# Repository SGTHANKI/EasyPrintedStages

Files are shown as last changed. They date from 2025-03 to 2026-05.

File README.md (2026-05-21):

# EasyPrintedStages
A set of 3D printed open sourced motion stages for scientific and laboratory work compatible with the gridfinity standard. The latest "stable" (version printed and tested) release can be found on the printables linked below. Please consider going there and like/download as it helps me out!
There are two different compatible stages in this ecosystem, a linear and rotary stage. A Z stage, pitch stage, and motorised stages are currently under development. You may see those in this repo but they are "alpha" versions uploaded to the master branch for collaborators to test before we fully release them. 

This readme is long but includes all the instructions you need to build and assemble the stages. __IF PRINTING A LINEAR STAGE CHECK THE LEADSCREW PRINTING GUIDE FIRST FOR BEST RESULTS__.
# Content:
- Build Options for All Stages
- Linear Stage Specific Build Options
- Linear Stage Printing Instructions
- Linear Stage Assembly Instructions
- Rotary Stage Prtinting Instructions
- Rotary Stage Assembly Instructions
- Motorised Stage Instructions

# Build Options for All Stages:
The design is built to be as modular as possible and users are encouraged to download FreeCAD and export the model to 3mf files for printer directly from the CAD files instead of using those provided. Numerous mounting solutions are also provided for the stage. 
## Optional Gridfinity Standard Mounting Plate:
The FreeCAD design makes use of the Gridfinity Workbench within FreeCAD. Users can find instructions on how to install and use this workbench under its associated page Gridfinity Workbench. A 2x2 unit Gridfinity base plate is provided in the design that can be screwed into the base of the stage. Additionally a 4x4 unit bolt together mesh is provided to act as a starting point for mounting a Gridfinity based stage system. 
Pasted image 20250202160743
Mounting bolts for the Gridfinity base plate go through the magnet holes on the plate base. __Note: If you make a custom base larger than 2x2u, you will need to quickly pocket the holes all the way through the plate. This has already been done on the provided 2x2u base.__
Easy Stage In Mesh Cover 1
## Optional Top Plate
Pasted image 20250202161026
An optional top plate can be printed with the design. It mounts via 4 M3 bolts in the corners of the plate. The other 2 holes in the plate are for locking bolts, these holes go all the way through the top plate of the stage and allow a longer 25mm M3 bolt to be tightened down into the base of the stage, locking it in place. This can be used to lock the stage in a desired position. 

The mounting plate features a grid of 2.6mm diameter holes, these are the perfect size for M3 bolts to thread into without the need for threaded inserts. The holes are spaced 5mm apart to make designing custom mounting hardware as easy as possible. Some hardware for this plate has been provided, namely the Easy Stage Clamp. 
### How to make a custom mounting plate:
Open the design in FreeCAD and activate the Mounting Plate Body. The final operation is the one that pockets all the mounting holes, simply deleting this operation or copying the body from the previous operation will yield a blank plate that can be modified however is 
Pasted image 20250202161508
Pasted image 20250202161528
## How to Mount Other Stages From The Ecosystem:
All of the Easy Printed Stages can be mounted to each other via the holes on their top.
Cover Linear Best
__NOTE ON ROTARY STAGE__ Only two mounting bolts are accessible, these should be more than enough to hold it down but because of how the case halves are tightened down together a second pair of holes would never line up. 
# Linear Stage Specific Build Options:
##Rubber Band For Anti-Backlash
You can loop a rubber band between the threaded nut and the two holes where the adjustor protrudes from the base to apply a constant force onto the lead screw. This is generally not needed if printed at higher tolerance but was included for users using older printers without input shaping. 

# Linear Stage Printing Instructions:
The design should be printed in 2 separate sets. These are documented here. __PLEASE CHECK THE LEAD SCREW SETTINGS BELOW OR IT WILL FAIL TO PRINT!__
## Bulk, Low Tolerance Components
Parts in this set are: 
- Base Plate with Integrated Gridfinity
- Shim
- Upper
- Adjuster Cap
- Base
- M3 5mm Spaced Mounting Plate
- 2u Gridfinity Base Plate

__Recommended Materials for This Set:__
- PETG --> Best overall and chemically resistant so good for use in the lab. 
- PETG CF --> Much stronger than regular PETG but surface is rougher and parts can be less clean/may need sanding. Also more expensive.
- PLA --> Cheapest and easiest to print but not chemically resistant so use only in non-wet lab's. 

You can also use pretty much anything else you want provided its mechanically hard but increasing the strength of these parts does little for the designs overall strength since the weakest point is the printed lead screw. 

__Print Settings and Other Info:__
- You can get away with a 0.6 or 0.8mm nozzle on this set to improve print time but the fit/finish will be worse. __0.4mm is recommended__. There is no need to use high detail slicer parameters. 
- __Enable support__ for the Base and Base Plate with Integrated Gridfinity parts, the overhand here needs it. Tree supports are recommended and if a __threshold angle of 30 degrees__ is used in the slicer only this region of the design will be supported by Tree's. //this was tested in Bambu, Orca, and Prusa slicer. 

3mf project files for this set have been made for Bambu Studio (specifically for the A1 Mini but can easily be adapted to their other printers) and Prusa slicer, they can be found within the GitHub for the project. 
## High Tolerance Threaded Parts
Parts in this set are: 
- Adjuster
- Thread Block Modelled

__Recommended Materials for This Set:__
- PETG --> Best if you only have a low temperature printer.
- ASA --> Best if you have a high temperature printer but chemical resistance isn't a concern. 
- PET --> Best for high temperature and chemical resistance but hard to print well. 

*Note on PLA: You can use it but it may not be strong enough nor is it chemically resistant.* 

*Note on CF/GF reinforced filaments: They can be used here but there is a concern about their abrasive nature wearing down the threads over time.* 

__Print Settings and Other Info:__
- Use a 0.4 or 0.2mm nozzle.
- Use 100% infill.
- Use the highest detail setting on the slicer of your choice, less because of detail, more because it will slow the printer down making the long tall lead screw print easier. 
- If you cannot use the provided 3mf for the Adjuster __HAVE A LOOK AT IT FIRST BELOW__. Custom painted on supports are used to stabilise the tall and wobbly part and make it print well. Open that model and see how I've done it before trying to print it yourself. I used the paint on custom support tool in the slicer with the tree supports. Make sure not to paint them onto the threads or it will ruin the threads, paint them on just after the threads finish at the top of the adjuster. 
Supported Leadscrew
Support Enforcers on Outside of Leadscrew
Support Enforcer in Top of Leadscrew

# Linear Stage Assembly Instructions:
## Important Note: 
Use silicone grease on the way and lead screw to make the stage move easier and last longer. 
## Step 1: Thread the Adjuster
Apply a small amount of Silicone Grease to the adjuster tip and to the holes made for it in the base of the stage, thread the adjuster through the block and then apply the end cap with an M3x5mm bolt. At this stage you should also apply Silicone Grease to the ways of the stage. You're assembly should look like the one seen below:
Step 1 Photo
__Note: The direction of the little triangle on the top of the thread block doesn't matter, its for a different project that re-uses these parts.__
## Step 2: Mount Upper
Insert the longer M3 bolts into the side of the upper but leave some space, you only want about 2mm of the bolt to protrude into the way, as seen below: 
step 2 alt angle photo
Slide the upper over the lower assembly from __STEP 1__, you dont need to put the shim in yet. You'll feel the top seat itself down onto the threaded block with a click, once you feel this you can tighten the two M3 bolts on the top.
step 2 no way
__Note: There is a vernier gauge modelled on the side of the base and the top piece, make sure you have the top piece the right way round if you plan on using these. The top is ambidextrous so if you get this wrong the stage will still work.__ 
You can now slide the shim in, make sure the holes on the side of the shim face the bolts you partially inserted earlier.
step 2 way insert photo
Slide the shim all the way in and then start to tighten the bolts on the side. 

__Important:__ Tighten each bolt a little at a time alternating between them. After each bolt check to see if moving the stage is hard, if its hard to move you've tightened the bolts too much and should back them off about half a turn. These bolts are what constrain the stage, you want no play (wobble) in the top of the stage but still want to be able to move the stage with little/no resistance. 
step 2 way flush
## Step 3: Mount Any Addons
You can now mount the top plate of a Gridfinity base. In the images above the Gridfinity base was already installed. You're finished stage should look something like this:
Easy Stage Linear Cover Photo
__Note: The stage shown in the image has been etched with a fibre LASER to engrave the text and decals seen__ 

# Rotary Stage Printing Instructions
## Cycloid 
Print the cycloid in PETG (or any other hard material thats not fiber reinforced). Use a 0.4mm or 0.2mm nozzle and high quality print settings. __NO SUPPORT IS NEEDED__
## Worm Gear
Generally the automatic organic supports of most modern slicers can print the work gear just fine with no needed additions. Print with a 0.4 or 0.2mm nozzle (ideally 0.2mm to make the action smoother). See the image below for how it was supported during testing. Printing at 100% infill is recommended for durability but not strictly necessary.
Pasted image 20250216155126
## All Other Parts
These can be printed in any material with either a 0.4 or 0.6mm nozzle. For the parts seen in the Easy Rotary Stage Assembly Instructions below, PETG-CF filament was used with a 0.6mm nozzle. 

# Rotary Stage Assembly Instructions:
## Important Note: 
Just as with the Linear Stage: Silicone Grease is your friend, use more than you think and wipe the excess off after! This stage can bind when first assembled due to small printing defects, spin the stage via the platform not the adjuster a few time to wear those defects down and smooth the action of the stage. 

## Step 1: Mount the Cycloid Gear
Mount the cycloid gear as seen below. The triangle embedded onto the base of the triangle and on the base of the stage will aid in alignment.

__DO NOT FULLY TIGHTEN THE BOLTS.__

Leave about 3mm space between the gear and the base plate. You tighten these later once the rest of the stage is installed. 
Gear Only On Top
Side Cinematic View

## Step 2: Slide the Front Under the Gear
You can now tighten the bolts on top so that there is no play between the cycloid gear and the front of the stage.
Cycloid Gear Installed

## Step 3: Insert the Worm Gear Into the Back Piece with the Spacer Shim
Slide the worm gear into the back of the case. See the pictures below. Its had to see the spacer, its the small "puck" looking part with a small indent on one side, this indent faces away from the worm gear and is pressed against by an M3 bolt which compresses the worm gear to prevent play in the mechanism. 
Shaft Installed Dark
__ENSURE THE SPACER PUCK IS BETWEEN THE WORM GEAR AND THE CASE__
The depression in the centre of the puck should face the case not the worm gear. An M3 bolt screws through the side of the case and pushed against this, removing the play in the cycloid gear. 
Adjustor Shim View
Its hard to see in the image below but an M3 bolt screws into that hole to compress the worm gear and remove any play in the mechanism. 
SIde Adjustor BOlt
## Step 4: Bolt the Front and Back of the Case Together
Assembled Mechanism Top View
There are two M3 counter bored holes on the worm gear side of the casing. Into these two M3 bolts can be placed that will mate with the other side of the case. Tighten these until the two halved are together and can move freely with no play. You may need to adjust this over time as the gears wear into each other. Avoid over tightening. This design will always have backlash due to the lower tolerances on the cycloid gears that make it possible. 

__You will need a long Hex Bit to reach the M3 bolts__
Lower Fully Assembled

## Step 5: Mount the Aligner Plate
The plate with two channels on it fits into the grooves on the front and base parts of the case, there are two bolt holes that lock this into the case and then prevent any movement. These are M3 bolts and have counter bored holes. The other holes in this piece are for either the Gridfinity Standard mounting plates, to mount the box to other Easy Printed Stages, or to mount a universal mounting plate. 
Top Bolted On Best

## Step 6: (OPTIONAL) Mount to Other Stages, Gridfinity Base, Mounting Plate etc..
Cover Gridfinity 4

# Motorised Stage Upgrade


## Build Differences
Under the "Motorised Linear Stage" Folder a different lead screw and base can be found for the standard linear stage. Follow the standard linear stage build instructions but replace the normal lead screw and base with the motorized versions. 

## Motors
The Motorised lead screws will directly interface with any standard 28BYJ stepper motor. The fit is designed to be tight and you may need to heat the lead screw to get it on. It is reccomended a small dot of some form of glue is used to prevent it loosening over time and with use.

## Endstops
Also provided are brackets for Cherry MX Mechanical keyswitches, but the design files are all provided in FreeCAD and anyone can design their own mount for a switch of their choice using the provided mounting holes on the base. Cherry MX switches were used as they are common and cheap but a future planned upgrade is to add a mount for the more precise and compact Omron SS-01. 

## Control System
Currently no electronics or control are provided though this is being worked on in a different repo that will be linked here when published. The 28BYJ motor is very sommon however and numerous arduino, micropython and C libraries exist to control it. Mounting solutions for darlington array style drivers and a base to contain them are provided. Pictured below are the venerable ULN2003 drivers that are commonly shipped alongside the motors, these are reccomended. 


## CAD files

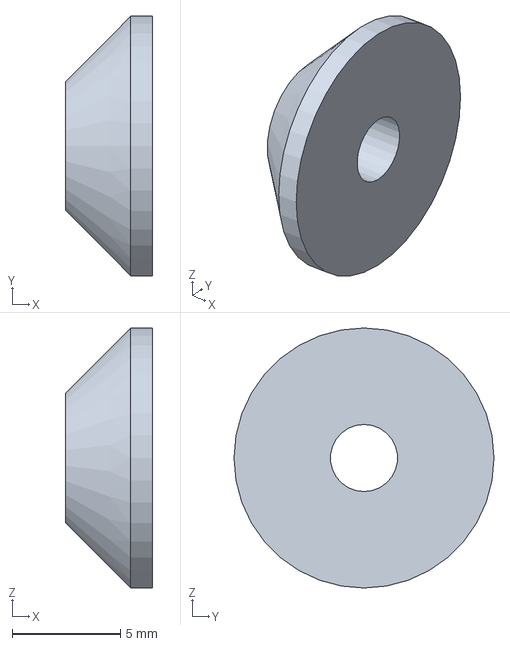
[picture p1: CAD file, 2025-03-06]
Clamp For Aluminium Extrusion/3mf Files/20mmAluClampPV1-Spring Retainer.3mf
4.00 x 12.0 x 12.0 mm

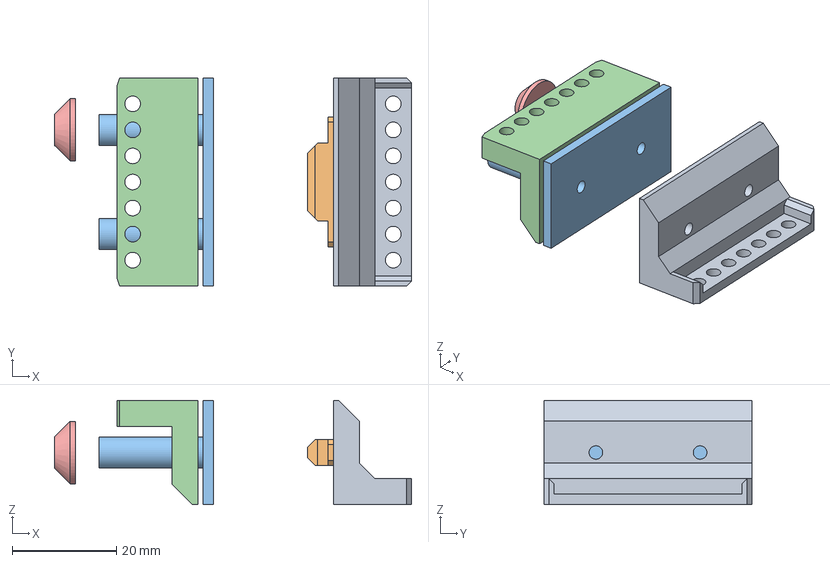
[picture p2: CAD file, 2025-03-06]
Clamp For Aluminium Extrusion/STEP Files/20mmAluClampPV1.step
68.5 x 40.0 x 20.0 mm
Clamp Back Plate
Extrusion Lug
Clamp Face
Clamp Body
Spring Retainer

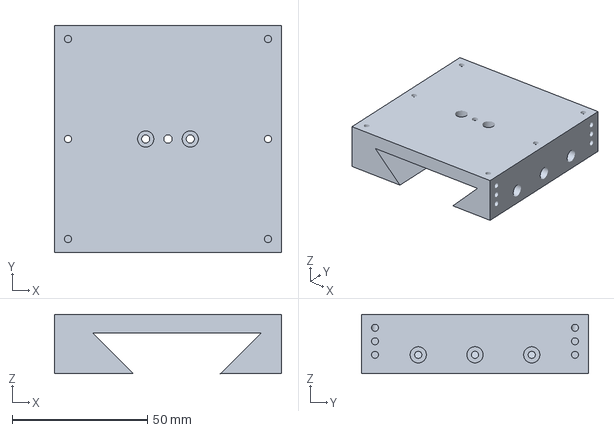
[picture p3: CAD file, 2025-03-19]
Linear Stage Fully Printed/3MF Files/Linear Stage Multi Part v5-Upper.3mf
84.0 x 84.0 x 22.0 mm

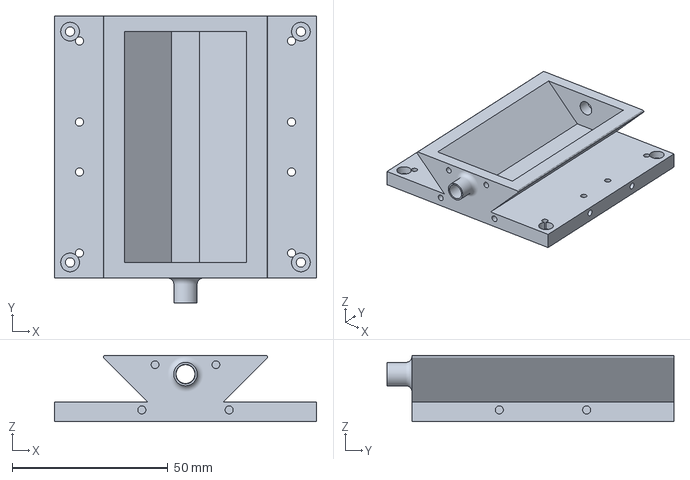
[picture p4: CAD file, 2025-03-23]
Linear Z Stage Fully Printed/3MF Files/Linear Stage Z Version-Base.3mf
84.0 x 92.0 x 21.2 mm

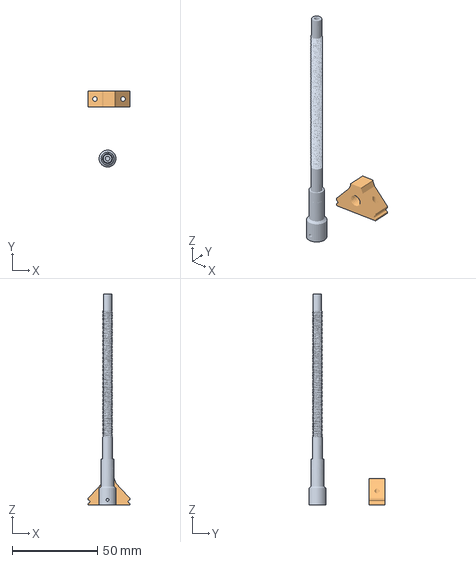
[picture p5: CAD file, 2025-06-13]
Motorised Linear Stage/Basic 3MF Files/Linear Stage Motorised-Adjuster.3mf
24.5 x 44.8 x 124.0 mm

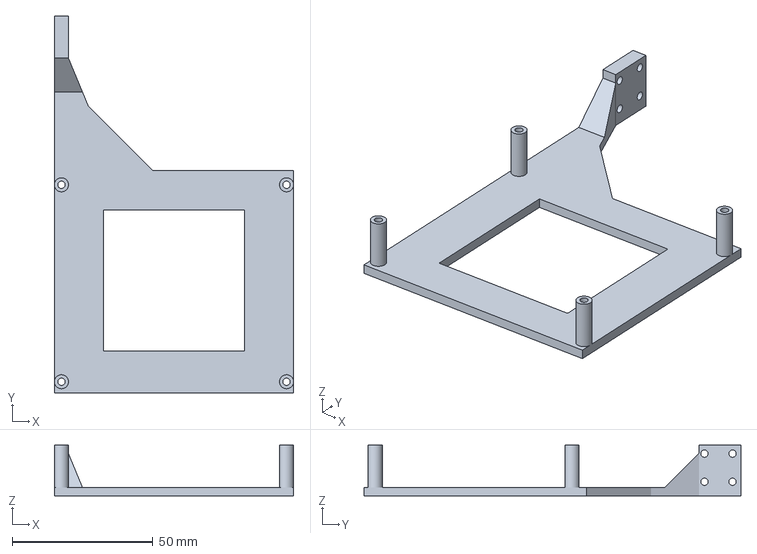
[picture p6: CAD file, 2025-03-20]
Motorised Linear Stage/Example Use Case Magnetic Field Mapping/3MF/Linear Stage Motorised B Field Version-V1 Driver PCB Mount.3mf
85.0 x 134.0 x 18.0 mm

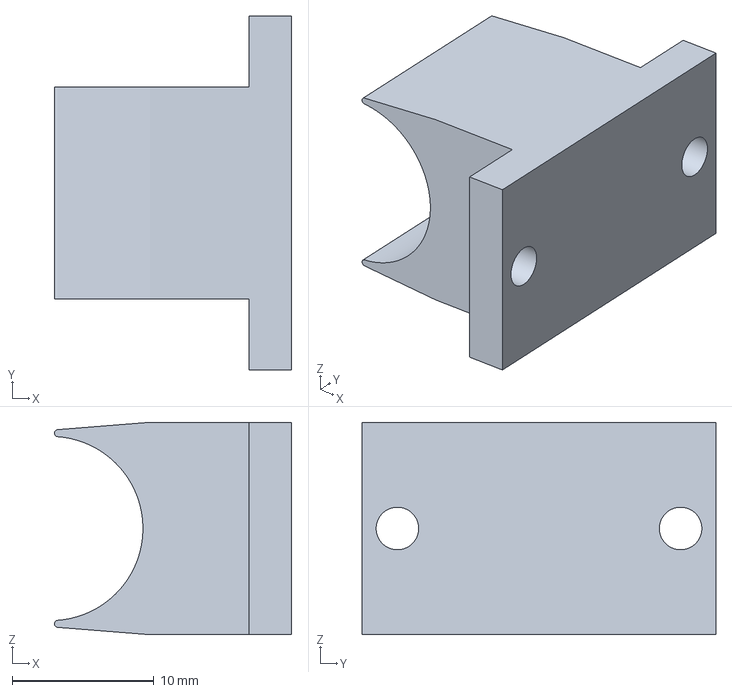
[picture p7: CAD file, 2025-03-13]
Motorised Linear Stage/Example Use Case Magnetic Field Mapping/Magnetic Field Probe Holder/3MF Files/Field Probe Clamp-Extrusion Lug.3mf
16.7 x 25.0 x 15.0 mm

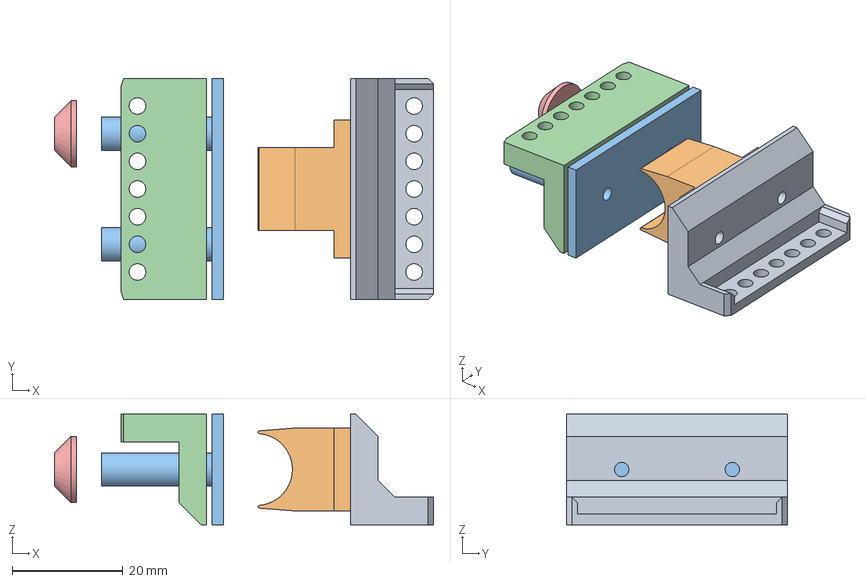
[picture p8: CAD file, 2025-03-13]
Motorised Linear Stage/Example Use Case Magnetic Field Mapping/Magnetic Field Probe Holder/Field Probe Clamp.FCStd
68.5 x 40.0 x 20.0 mm
Clamp Back Plate
Extrusion Lug
Clamp Face
Clamp Body
Spring Retainer

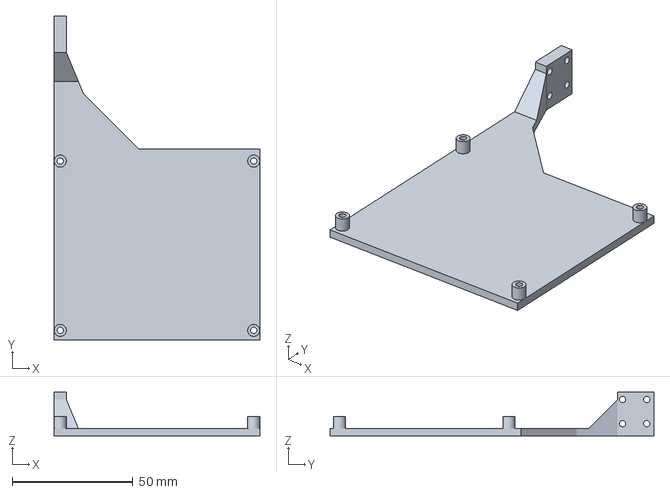
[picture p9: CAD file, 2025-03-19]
Motorised Linear Stage/Magnetic Field Probe Holder/3MF Files/Linear Stage Motorised B Field Version-V1 Driver PCB Mount.3mf
85.0 x 134.0 x 18.0 mm

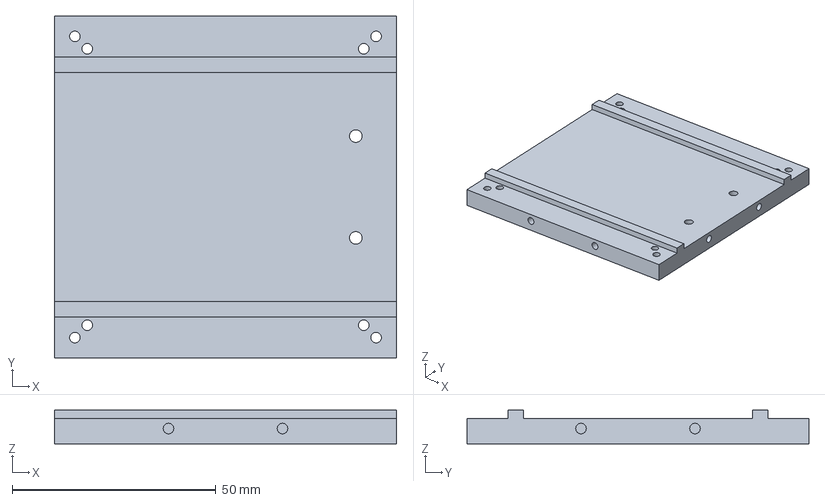
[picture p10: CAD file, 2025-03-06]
Rotary Stage Fully Printed/3mf Files/Rotary Stage v2-Base Plate.3mf
84.0 x 84.0 x 8.25 mm

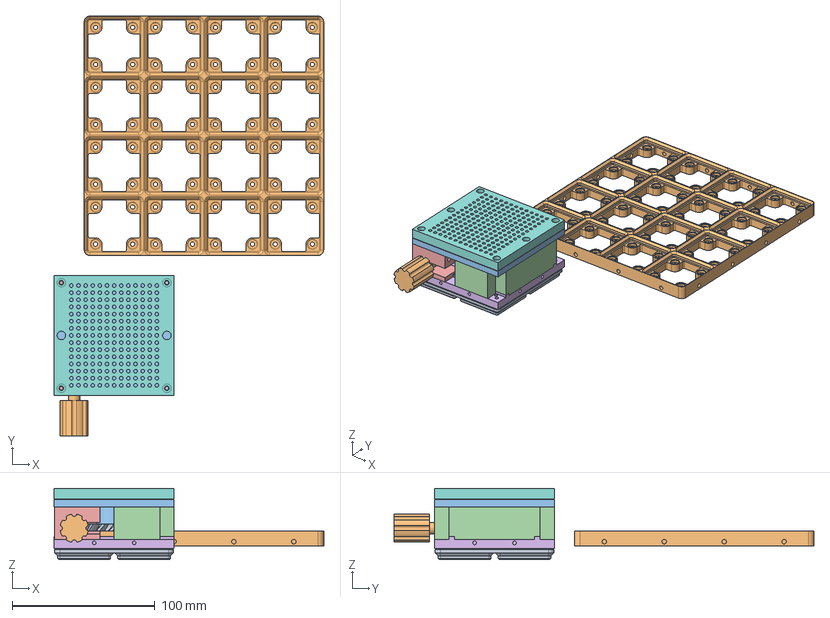
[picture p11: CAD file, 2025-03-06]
Rotary Stage Fully Printed/STEP Files/Rotary Stage v2.step
189.0 x 294.5 x 49.9 mm
Cycloid Gear
Worm Gear Adjustor
Top Plate
Midplate A
Midplate B
Base Plate
Worm Gear Spacer
M3 5mm Spaced Mounting Plate
Gridfinity Base Plate
Screw Together Mesh

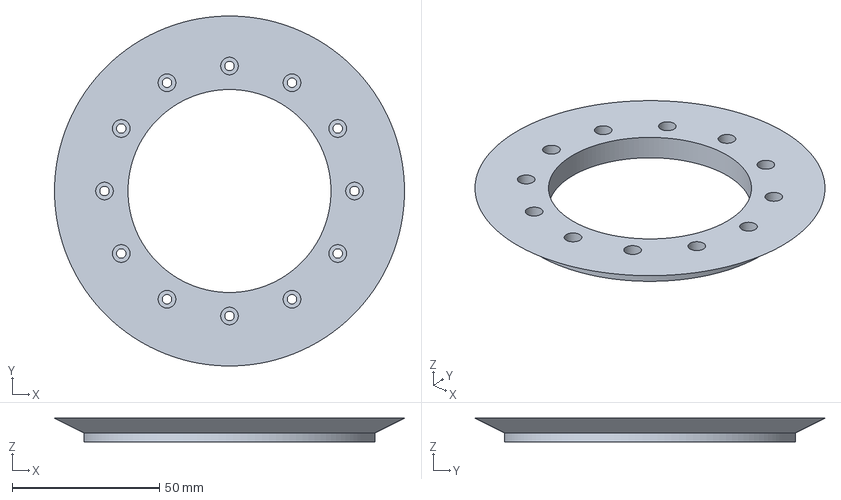
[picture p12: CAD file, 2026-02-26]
Rotary Stage V2/Rev 1 Test Prints/SlewingRingRev1-InnerUpper.3mf
119.0 x 119.0 x 8.00 mm

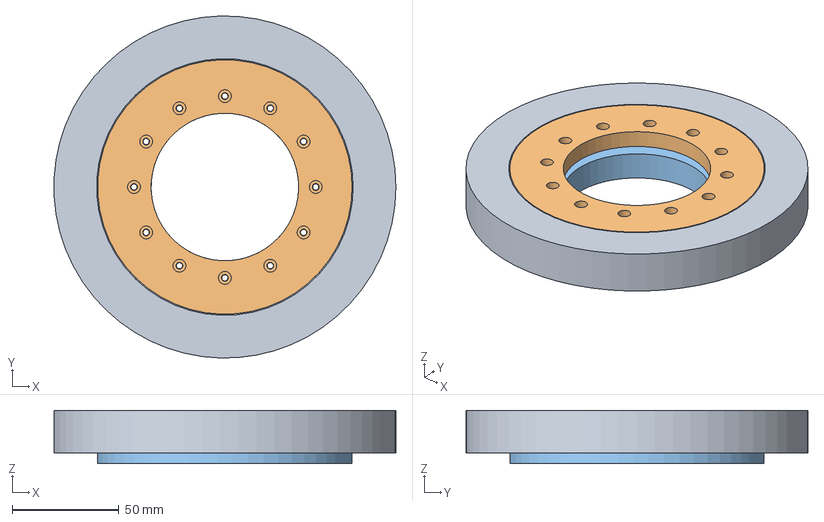
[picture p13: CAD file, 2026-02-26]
Rotary Stage V2/SlewingRingRev1.FCStd
159.9 x 159.9 x 25.0 mm
InnerUpper
InnerLower

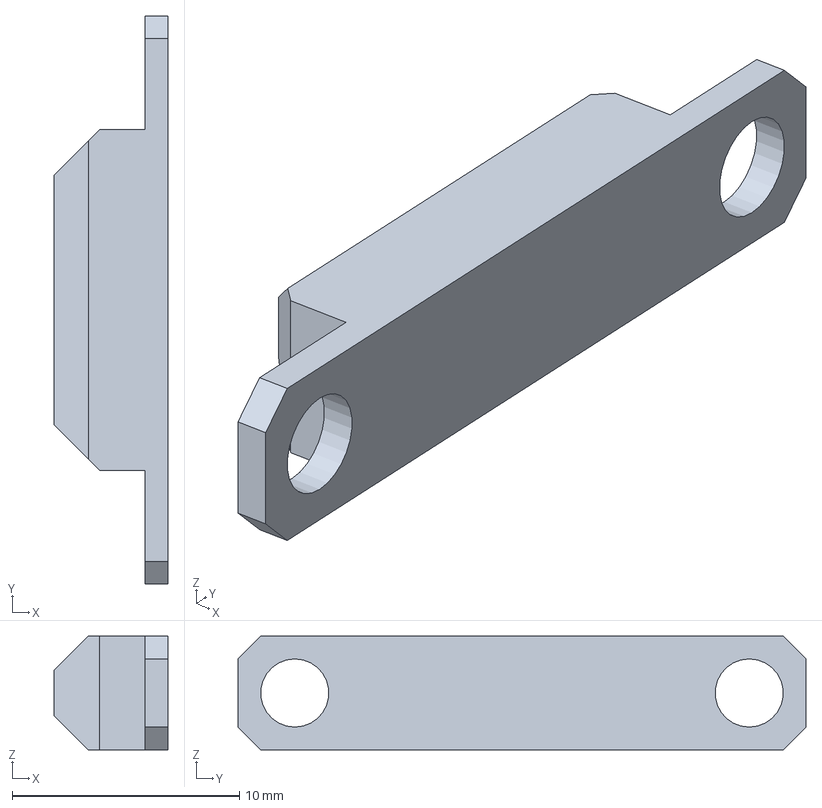
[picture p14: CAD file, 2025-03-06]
Clamp For Aluminium Extrusion/3mf Files/20mmAluClampPV1-Extrusion Lug.3mf
5.00 x 25.0 x 5.00 mm

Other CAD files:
Motorised Linear Stage/Example Use Case Magnetic Field Mapping/FieldProbeAssembly.FCStd
Linear Stage Fully Printed/3MF Files/Linear Stage Multi Part v5-Adjuster With Supports.3mf
Linear Z Stage Fully Printed/3MF Files/Linear Stage Z Version-Thread Block Modelled.3mf
Motorised Linear Stage/Basic 3MF Files/Linear Stage Motorised-Adjuster bambu supported.3mf
Bolt Down Brackets/3mf Print Files/Bolt Down Brakets-Easy Stage Bolt Down.3mf
Bolt Down Brackets/Bolt Down Brakets.FCStd
Bolt Down Brackets/STEP Files/Bolt Down Brakets-Easy Stage Bolt Down.step
Clamp For Aluminium Extrusion/3mf Files/20mmAluClampPV1-Clamp Back Plate.3mf
Clamp For Aluminium Extrusion/3mf Files/20mmAluClampPV1-Clamp Body.3mf
Clamp For Aluminium Extrusion/3mf Files/20mmAluClampPV1-Clamp Face.3mf
Linear Stage Fully Printed/3MF Files/Linear Stage Multi Part v5-Adjuster Cap.3mf
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

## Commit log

2025-01-25 Uploaded CAD Model
    Uploaded the v5 (current latest) model for the linear stage and also formatted the repo with some files.
2025-01-26 Added 3MF for printing from v5 latest
    Added 3mf files for the latest v5 linear stage model and renamed some parts within to make identification easier as standalone 3MFs.
    [Linear Stage Multi Part v5-2u base plate.3mf, Linear Stage Multi Part v5-Adjustor Cap.3mf, Linear Stage Multi Part v5-Adjustor.3mf, Linear Stage Multi Part v5-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]
2025-01-26 New naming on parts and STEP format added.
    New names for the sub components have been added to make writing the documentation easier. STEP exports of this version of the project were also included though these are not intended as the primary 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
    [Linear Stage Multi Part v5-2u Gridfinity Base Plate.3mf, Linear Stage Multi Part v5-2u base plate.3mf, Linear Stage Multi Part v5-Adjustor Cap.3mf, Linear Stag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]
2025-01-30 Fixed Gridfinity Base
    Properly made the base with holes in it and added an example 4x4 gridfinity mesh.
    [Linear Stage Multi Part v5-2u Gridfinity Base Plate.3mf]
2025-02-01 Added Rotary and Re Expored 3mf in linear
    Added rotary and brought it up to speed with the rest of the designs.
    [Linear Stage Multi Part v5-2u Gridfinity Base Plate.3mf, Linear Stage Multi Part v5-Adjuster Cap.3mf, Linear Stage Multi Part v5-Adjuster.3mf, Linear Stage Mul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]
2025-02-02 Changed Way M3 Hole Diameter
    Previous Version had it at 3mm, changed it to 2.65mm to make M3 screws usable.
2025-02-06 added supported version
    added supported version of 3mf
    [Linear Stage Multi Part v5-Adjuster With Supports.3mf]
2025-02-08 Added 3mf print files
    Added 3mf print file and a bambu a1 mini project file for it all.
    [Bambu A1 Mini Print Project File.3mf, Rotary Stage v2-Base Plate.3mf, Rotary Stage v2-Cycloid Gear.3mf, Rotary Stage v2-Gridfinity Base Plate.3mf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]
2025-02-09 Update Bambu A1 Mini Print Project File.3mf
    [Bambu A1 Mini Print Project File.3mf]
2025-02-16 Added Aluminium Clamp
    Added the spring loaded aluminium extrusion clamp design for 20mm aluminium.
    [20mmAluClampPV1.FCStd]
2025-02-16 Added Bambu SLicer Print File for Rotary Stage
    [Bambu A1 Mini Print Project File.3mf]
2025-02-16 Added 3MF for clamps
    [20mmAluClampPV1-Clamp Back Plate.3mf, 20mmAluClampPV1-Clamp Body.3mf, 20mmAluClampPV1-Clamp Face.3mf, 20mmAluClampPV1-Extrusion Lug.3mf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]
2025-02-16 added step file
    [Rotary Stage v2.step]
2025-02-16 added steps
    [20mmAluClampPV1.FCStd, 20mmAluClampPV1.step]
2025-02-16 added fatter base to worm gear.
    [Rotary Stage v2-Worm Gear Adjustor.3mf]
2025-02-17 Bolt Down Bracket Update
    Made base of rotary stage fatter so its equal to linear stage. Then designed bolt down brackets so they will fit both. Also added mounting holes for brackets on newly enlarged rotary stage.
    [Bolt Down Brakets-Easy Stage Bolt Down.3mf, Bolt Down Brakets.FCStd, Rotary Stage v2-Base Plate.3mf]
2025-02-17 Added step
    [Bolt Down Brakets-Easy Stage Bolt Down.step, Rotary Stage v2.step]
2025-02-19 added pdf instructions from printables
2025-03-06 Designed Motorised Stage
    [Linear Stage Motorised-Adjuster.3mf, Linear Stage Motorised-Base.3mf]
2025-03-08 added bambu 3mf project
    added a bambu 3mf project with sliced adjuster piece and added supports.
    [bambu_supported Linear Stage Motorised-Adjuster.3mf]
2025-03-08 Aded Adjuster Cap 3mf
    Added Adjuster Cap 3mf
    [Linear Stage Motorised-Adjuster Cap.3mf]
2025-03-10 added prusa 3mf for everything but the adjuster
    added prusa 3mf for everything but the adjuster
    [prusa Linear Stage Motorised-everything_else.3mf]
2025-03-10 Added base mount and switch end stops with some extra mounting holes
    Added base mount and switch end stops with some extra mounting holes
2025-03-12 Added New 3MF files and fixed overhand on the stage base
    Added New 3MF files and fixed overhand on the stage base
    [Linear Stage Motorised-Base.3mf, Linear Stage Motorised-CherryMXHolder.3mf, Linear Stage Motorised-Motorised Stage Base.3mf, Linear Stage Motorised-Upper.3mf]
2025-03-12 Added field probe holding clamp to repo
    [Field Probe Clamp-Clamp Back Plate.3mf, Field Probe Clamp-Clamp Body.3mf, Field Probe Clamp-Clamp Face.3mf, Field Probe Clamp-Extrusion Lug.3mf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]
2025-03-12 Added more mounting options
    [Field Probe Clamp-Extrusion Lug.3mf, Field Probe Clamp.FCStd]
2025-03-13 new 3mf lug
    [Field Probe Clamp-Extrusion Lug.3mf]
2025-03-13 improved clamp
    [Field Probe Clamp.FCStd, Linear Stage Motorised-Button PCB Mount.3mf]
2025-03-13 resolved conflict and included assembly
    [FieldProbeAssembly.FCStd, Linear Stage Motorised-ULN2003 Module Mount.3mf]
2025-03-18 Moved the magnetic stuff to new examples directory + other stuff
    basically prepared the files for release, in freeCAD i changed positions and viewing angles of a few parts and made sure 3mf's were up to date.
    [Field Probe Clamp-Clamp Back Plate.3mf, Field Probe Clamp-Clamp Body.3mf, Field Probe Clamp-Clamp Face.3mf, Field Probe Clamp-Extrusion Lug.3mf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]
2025-03-19 Added PCB Mount part for the V1 PCB
    Please note this PCB is already outdated and the mounting system is likely to change.
    [Linear Stage Motorised B Field Version-V1 Driver PCB Mount.3mf]
2025-03-19 Added more mounting points for dual end stops.
    [Bambu Linear Stage Motorised Basic Parts.3mf, Linear Stage Motorised-Adjuster.3mf, Linear Stage Motorised-Base.3mf, Linear Stage Motorised-Upper.3mf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]
2025-03-20 Designed and Added Z stage adaptor for linear stage
    [Linear Stage Motorised B Field Version-V1 Driver PCB Mount.3mf, Linear Stage Z Version-Bolt On Z Adaptor.3mf]
2025-03-21 Added 5mm adaptors for Z stage
    [Linear Stage Z Version-90 Deg Plate to Plate.3mf, Linear Stage Z Version-90 Degree Plate Adaptor.3mf]
2025-03-21 Added modified 5mm mount adaptor
2025-03-23 Added New Support Piece to Base of Z stage to Prevent it falling over when loaded excessively
    [Linear Stage Z Version-Support Base Extension.3mf]
2025-03-23 Im proved the Z base extender so it sits flush
    [Linear Stage Z Version-Support Base Extension.3mf]
2025-03-23 Final Version before Printables upload with fixed extender and improve mounting system.
    [Linear Stage Z Version-90 Deg Plate to Plate.3mf, Linear Stage Z Version-90 Degree Plate Adaptor.3mf, Linear Stage Z Version-Adjuster Cap.3mf, Linear Stage Z V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]
2025-03-31 Added new 3mf files for printing latest stable motor stage
    [Linear Stage Motorised-5mm grid boltdown.3mf, Linear Stage Motorised-Adjuster Cap.3mf, Linear Stage Motorised-Adjuster.3mf, Linear Stage Motorised-Base.3mf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]
2025-04-15 New 3mf generated ready for release
    new 3mf with bulk part project ready for release.
    [All Bulk Parts Bambu Slicer.3mf, Bambu Linear Stage Motorised Basic Parts.3mf, Linear Stage Motorised-5mm grid boltdown.3mf, Linear Stage Motorised-Adjuster Ca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]
2026-02-25 Slewing Ring First Prototype
    Added a new rotary stage replacement based on a slewing ring design where parts slide instead of roll.
    [SlewingRingRev1.FCStd]
2026-02-26 3mf Exports added for v1 slewing Ring Test
    [SlewingRingRev1-Body.3mf, SlewingRingRev1-InnerLower.3mf, SlewingRingRev1-InnerUpper.3mf, SlewingRingRev1.FCStd]
2026-05-21 Update README.md
    Added motorized stage instructions
